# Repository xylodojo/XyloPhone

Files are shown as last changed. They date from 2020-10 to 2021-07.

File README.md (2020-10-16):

# XyloPhone
Design files and materials related to the XyloPhone platform. 

The preprint is available on bioRxiv: https://biorxiv.org/cgi/content/short/2020.08.02.233114v1

~~The manuscript is currently under review. After publication the design files for producing a XyloPhone will be disseminated here.~~

The paper has been accepted to the IAWA journal. It is an open access article and should be here (when it goes to "press"): https://brill.com/view/journals/iawa/aop/issue.xml

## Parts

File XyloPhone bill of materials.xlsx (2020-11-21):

 | XyloPhone Bill of Materials
Qty | XyloPhone part | Vendor | MFR | MFR # | Total cost | units per cost | cost per part | Cost per Scope
1 | LED controller | Digikey | Recom Power | RCD-24-0.30‎ | 13.46 | 1 | 13.46 | 13.46
1 | Voltage reference | Digikey | ‎Analog Devices Inc.‎ | AD680JTZ‎ | 5.75 | 1 | 5.75 | 5.75
1 | Radial capacitor | Digikey | Murata Electronics‎ | RDER71H104K0P1H03B‎ | 0.31 | 1 | 0.31 | 0.31
4 | White LED | Digikey | Lite-On Inc. | ‎LTPL-P00DWS57‎ | 0.76 | 1 | 0.76 | 3.04
4 | UV LED | Digikey | Vishay Semiconductor Opto Division | ‎VLMU1610-365-135CT-ND‎ | 2.38 | 1 | 2.38 | 9.52
1 | SPDT switch | Digikey | NKK Switches | MS13AFG01‎ | 4.05 | 1 | 4.05 | 4.05
2 | Right angle JST Through-Hole 2-Pin Connector | Digikey | JST Sales America | S2B-PH-K-S(LF)(SN) | 0.17 | 1 | 0.17 | 0.34
1 | JST jumper two wire assembly 6" | Digikey | Sparkfun Industries | PRT-09914 | 0.95 | 1 | 0.95 | 0.95
4 | 1/2" No. 2 screw | McMasterCarr | McMasterCarr | 95893A560 | 13.41 | 50 | 0.27 | 1.07
6 | 1/4" No. 0 screw | McMasterCarr | McMasterCarr | 95893A505 | 14.05 | 50 | 0.28 | 1.69
1 | Belomo 10x Triplet hand lens | belomostore.com | Belomo |  | 29.98 | 1 | 29.98 | 29.98
1 | battery | SparkFun | Lithium Ion Battery - 1Ah | PRT-13813 ROHS | 9.95 | 1 | 9.95 | 9.95
1 | charger | SparkFun | SparkFun LiPo Charger Plus | PRT-15217 | 9.95 | 1 | 9.95 | 9.95
1 | Reversible USB A to C Cable - 0.3m | SparkFun | SparkFun | CAB-15426 ROHS | 3.95 | 1 | 3.95 | 3.95
1 | Power distribution PCB |  |  |  | 5 | 5 | 1.00 | 1.00
1 | Power input PCB |  |  |  | 5 | 5 | 1.00 | 1.00
1 | Power output PCB |  |  |  | 5 | 5 | 1.00 | 1.00
4 | LED PCB |  |  |  | 5 | 5 | 1.00 | 4.00
 |  |  |  |  | 129.12 |  |  | 101.01

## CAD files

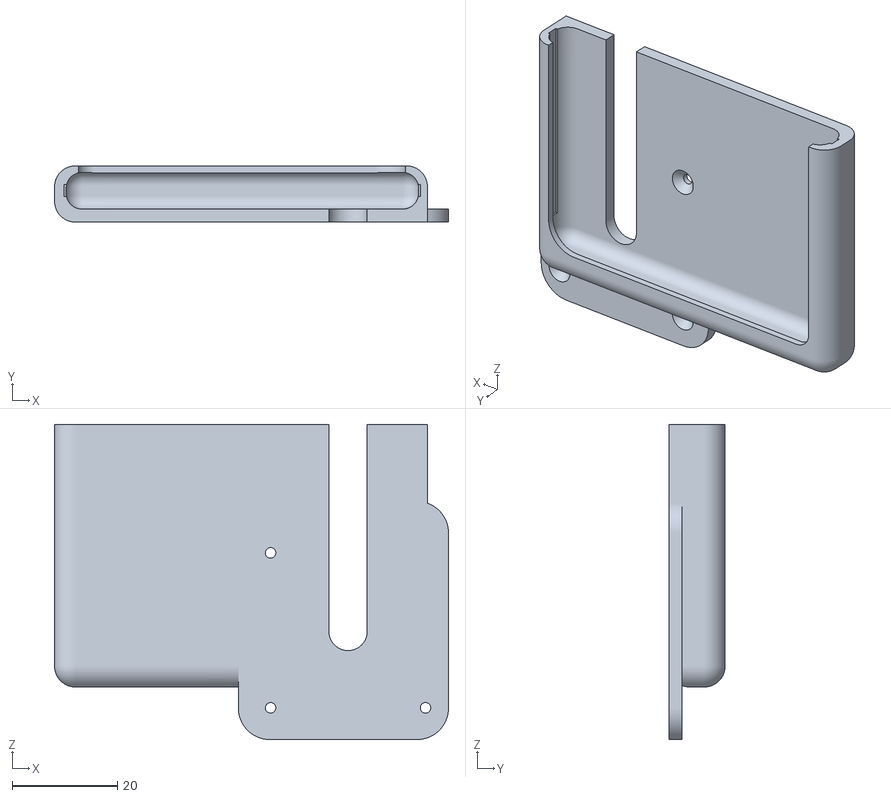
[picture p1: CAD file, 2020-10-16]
3D files/3D files/phone_adapters/iphone_6.stl
75.0 x 10.7 x 60.0

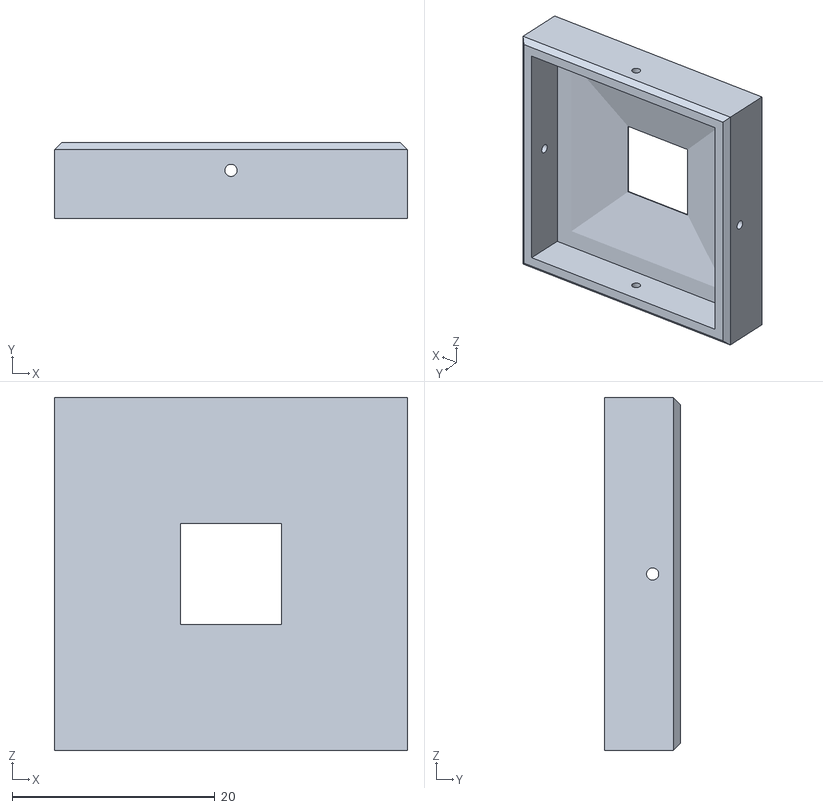
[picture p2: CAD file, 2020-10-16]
3D files/3D files/surface_plate.stl
34.8 x 7.50 x 34.8

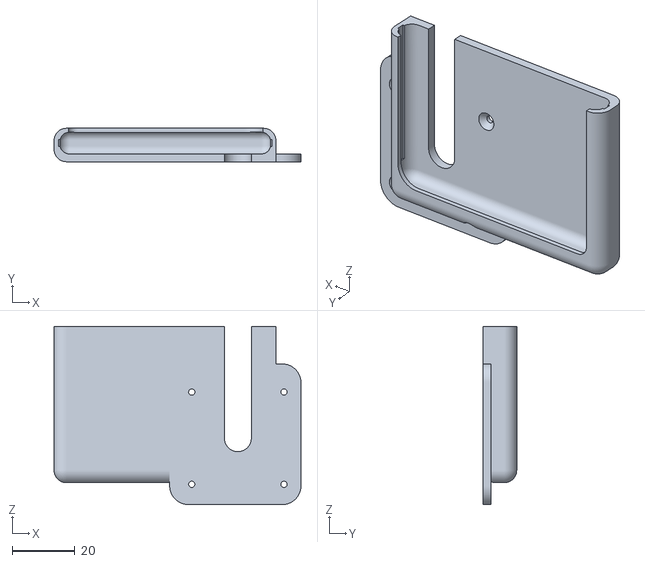
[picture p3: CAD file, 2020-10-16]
3D files/3D files/phone_adapters/iphone_8.stl
79.0 x 10.7 x 57.0

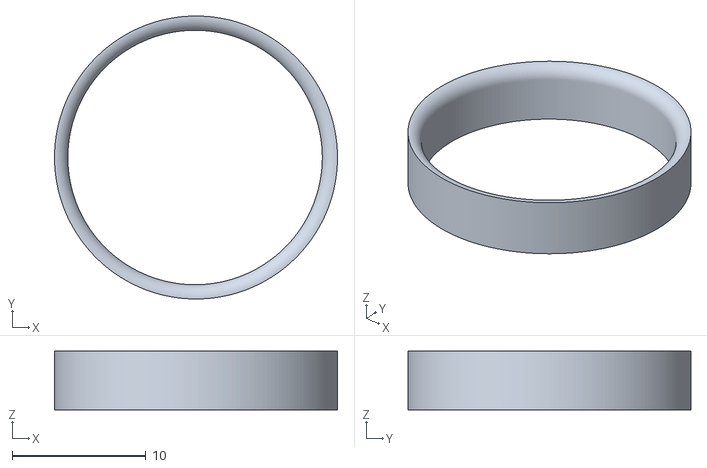
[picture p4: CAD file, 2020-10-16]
3D files/3D files/spacer_ring.stl
21.1 x 21.1 x 4.40

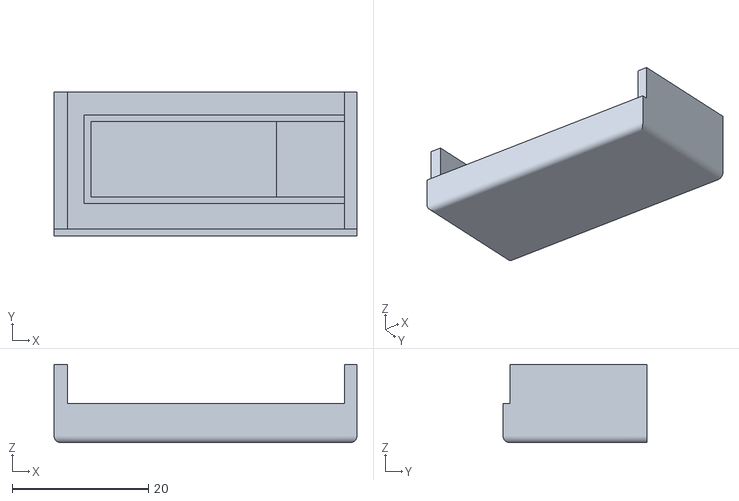
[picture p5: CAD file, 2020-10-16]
3D files/3D files/charger_cap.stl
44.4 x 21.1 x 11.5

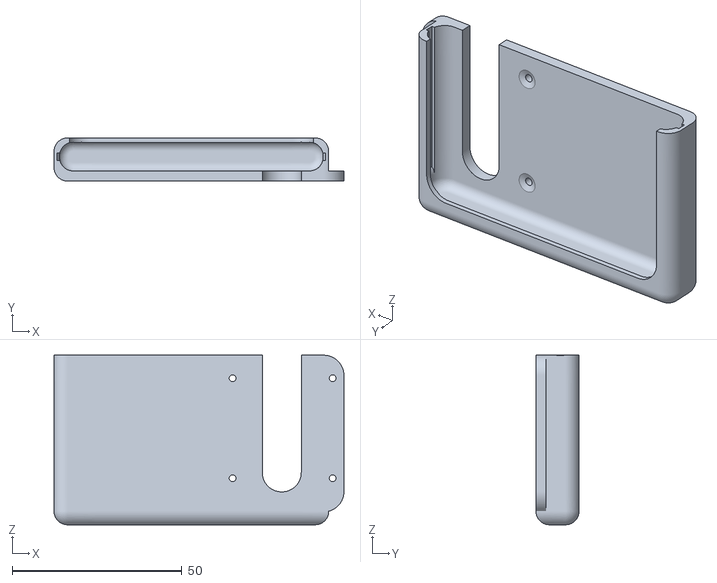
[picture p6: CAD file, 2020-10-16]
3D files/3D files/phone_adapters/iphone_XSMax.stl
85.5 x 12.7 x 50.0

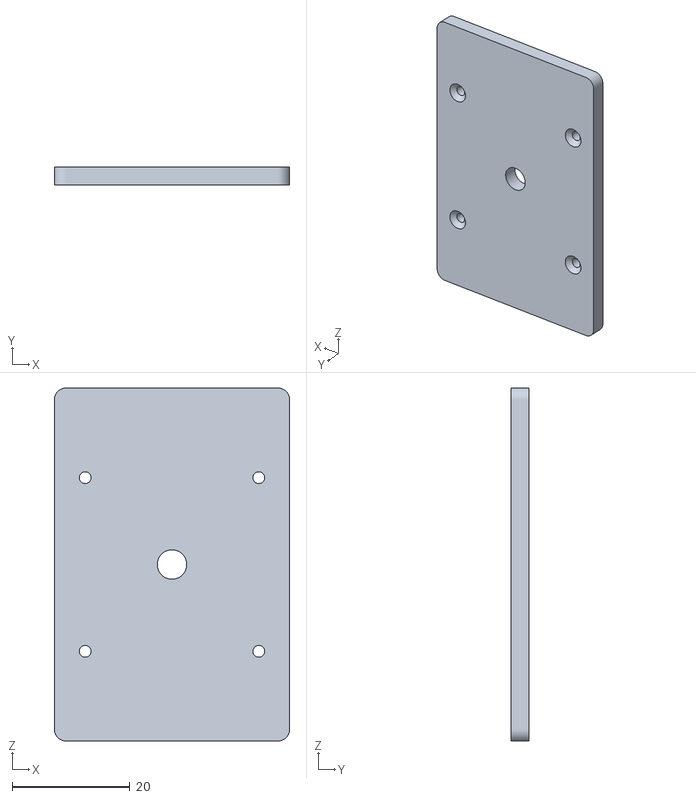
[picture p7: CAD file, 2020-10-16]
3D files/3D files/phone_adapters/generic_template.stl
40.0 x 3.00 x 60.0

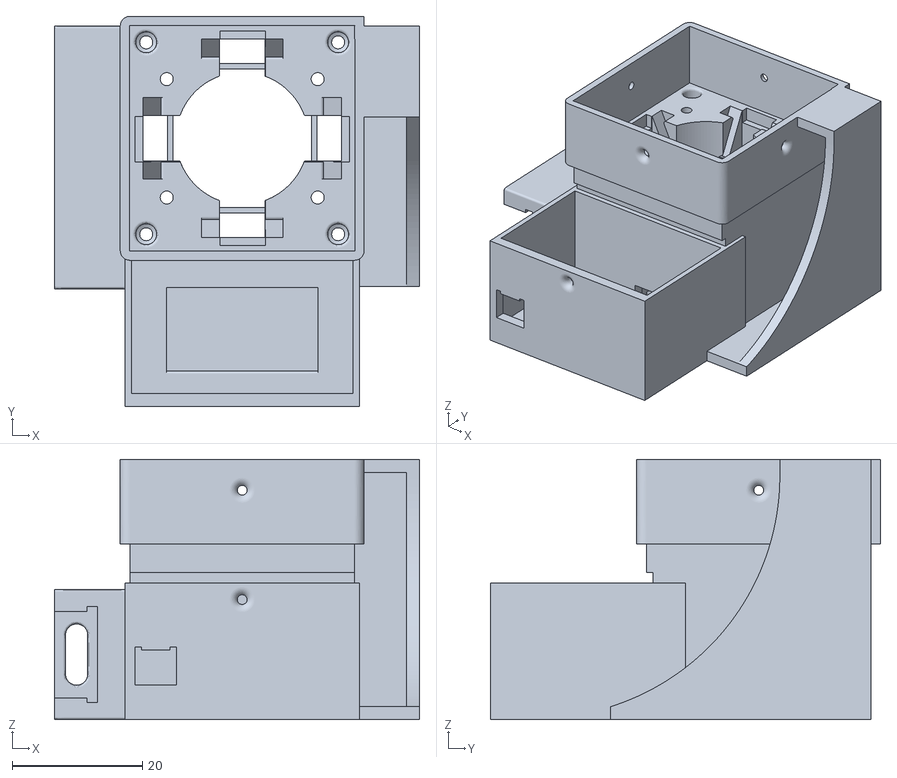
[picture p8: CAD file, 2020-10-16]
3D files/3D files/XyloPhone_housing.stl
56.1 x 60.0 x 40.0

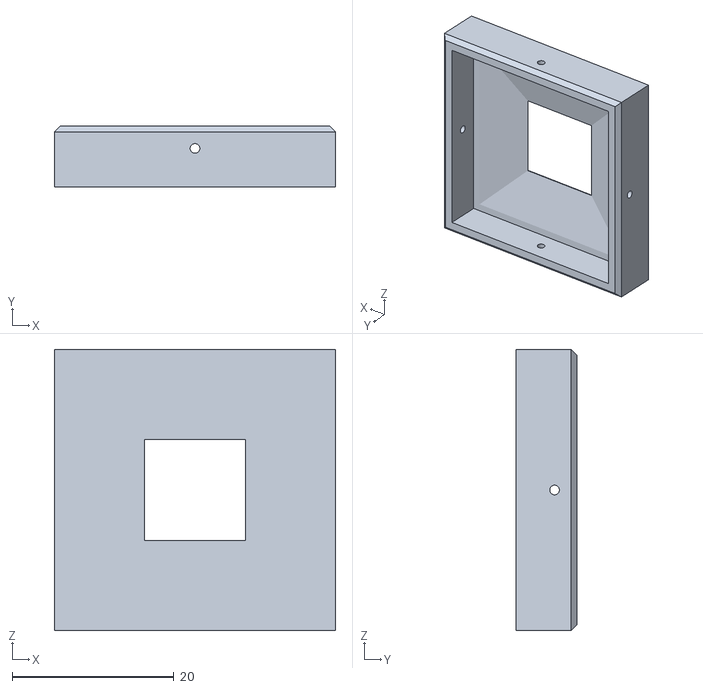
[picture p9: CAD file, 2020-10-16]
3D files/3D files/max_aperture_surface_plate.stl
34.8 x 7.50 x 34.8

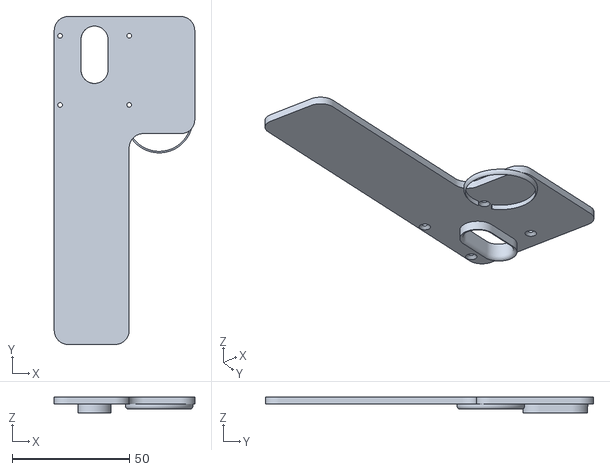
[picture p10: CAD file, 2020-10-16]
3D files/3D files/phone_adapters/iphone_XSMax_Otterbox_paddle.stl
60.0 x 140.0 x 6.70

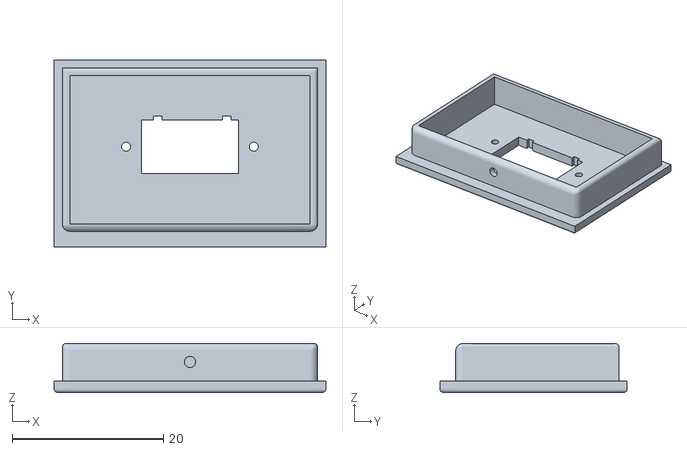
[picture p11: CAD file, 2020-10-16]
3D files/3D files/electronics_lid.stl
36.0 x 24.8 x 6.50

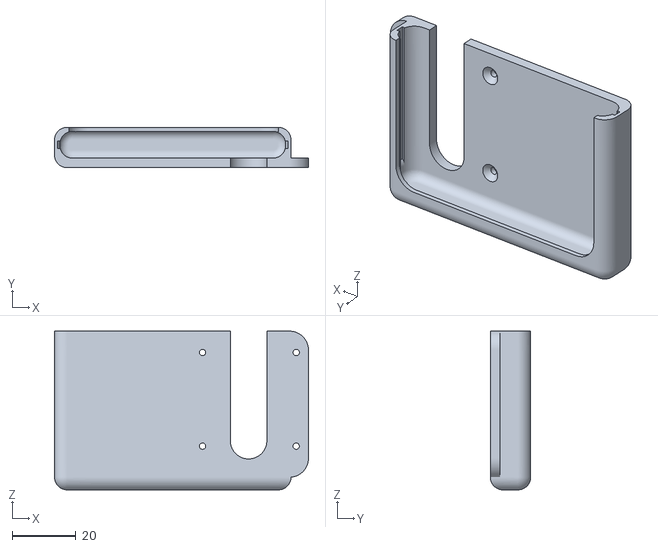
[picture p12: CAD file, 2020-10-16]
3D files/3D files/phone_adapters/iphone_XS.stl
80.0 x 12.7 x 50.0

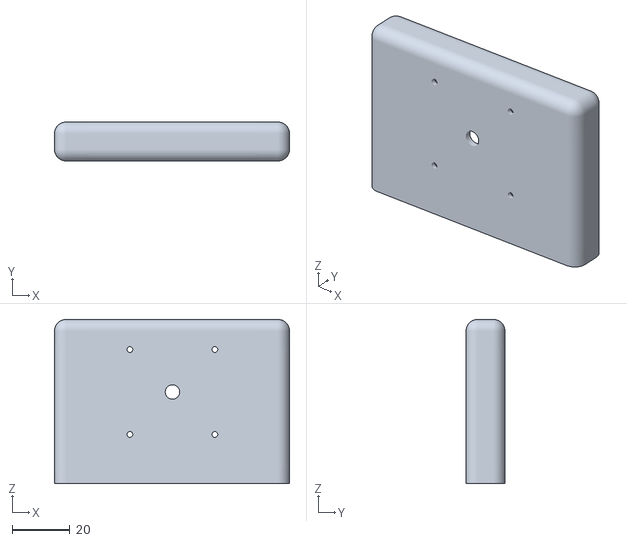
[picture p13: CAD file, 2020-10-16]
3D files/3D files/phone_adapters/samsung_Note5.stl
81.6 x 13.5 x 57.0

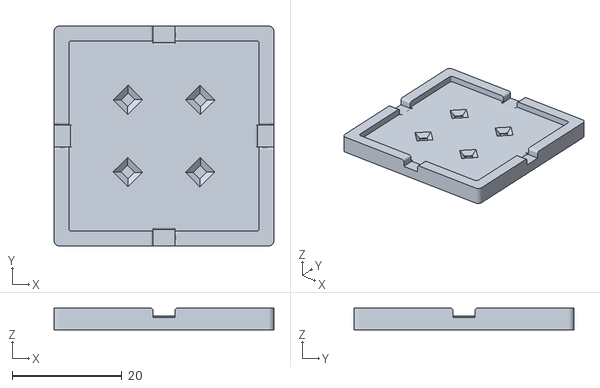
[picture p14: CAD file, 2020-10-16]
3D files/3D files/UV mounting jig.stl
40.0 x 40.0 x 4.00

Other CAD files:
3D files/3D files/phone_adapters/iphone_7Plus.stl

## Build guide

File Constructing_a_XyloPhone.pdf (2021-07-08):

# Constructing a XyloPhone

Alex C. Wiedenhoeft
Caitlin Gilly

Center for Wood Anatomy Research, Forest Products Laboratory US Forest Service, US Department of Agriculture

October 2020

Those portions of this manual recycled from the XyloTron assembly manual by Wiedenhoeft and Kleinschmidt (2020) are used here with permission of the authors.

TABLE OF CONTENTS

Part One: The Need for and Use of This Manual

Part Two: Bill of Materials

Part Three: Illustrated Parts List and Preparatory Work

Part Four: Step-by-Step XyloPhone Assembly and Calibration Instructions

PART ONE: THENEED FOR AND USE OF THIS MANUAL

The XyloPhone you are about to build is the next generation of imaging hardware for the broader XyloTron platform, leveraging the electronics of the XyloScope, but in a compact new design to accommodate bring-your-own-device functionality. The XyloPhone’s design reflects the intent that this device can be built by an enterprising end-user to image a wide range of substrates – it is an assemblage of individually simple off-the-shelf (itemized in the bill of materials in Part Two) and 3D printable components. With a phone-specific adapter it can be used on virtually any smartphone.

In Part Three we present an illustrated parts list and a short description of preparatory work that should be done prior to assembly. In this section we also note with an * several parts for which it is prudent to acquire more than the minimum number, because, if a mistake is made and the part is ruined, having spares facilitates the efficient completion of your XyloPhone. Fortunately, those components most likely to be ruined in the learning process are among the most affordable.

The step-by-step instructions in Part Four are relatively detailed. Despite this, the manual does assume certain basic skills. Specifically, no instruction on the use of basic tools (screwdrivers, cutting tools) is provided, nor is there any tutorial in stripping wires or soldering electronic components. Such tutorials abound (e.g. learn.sparkfun.com). We further assume basic functionality in 3D printing and that, if a printed component is faulty or damaged, such components can be readily reprinted.

This manual is intended to provide detailed instructions to assemble the XyloPhone in its current incarnation. It also lays the groundwork for a novice to make special modifications themselves to adapt the XyloPhone for the widest possible breadth of uses. We look forward to a future where other workers develop and share designs superior to what we provide here, and we hope to benefit from those advancements.

Each part or component is given a number in the illustrated part list. In the assembly instructions, the list number of each part is presented in parentheses beside the part’s name in the text so that should one experience any confusion, it can easily be remedied by consulting the list.

PART TWO: BILL OF MATERIALS

The bill of materials to build one XyloPhone. Minimum required quantity (Qty), XyloPhone part name, Vendor, Manufacturer (MFR), and manufacturer part number (MFR #) are listed. Please refer to the notes in Part Three for those parts for which acquiring more than the minimum possible number might be advisable. One will also need a smartphone, and to adapt a holder for that phone.

Qty | XyloPhone part | Vendor | MFR | MFR #
1 | LED controller | Digikey | Recom Power | RCD-24-0.30
1 | Voltage reference | Digikey | Analog Devices Inc. | AD680JTZ
1 | Radial capacitor | Digikey | Murata Electronics | RDER71H104K0P1H03B
4 | White LED | Digikey | Lite-On Inc. | LTPL-P00DWS57
4 | UV LED | Digikey | SunLED | XZVS54S-9A
1 | SPDT switch | Digikey | NKK Switches | MS13AFG01
2 | Right angle JST Through-Hole 2-Pin Connector | Digikey | JST Sales America | S2B-PH-K-S(LF)(SN)
1 | JST jumper two wire assembly 6" | Digikey | Sparkfun Industries | PRT-09914
4 | 1/2" No. 2 screw | McMasterCarr | McMasterCarr | 95893A560
7 | 1/4" No. 0 screw | McMasterCarr | McMasterCarr | 95893A505
1 | 1/4" No. 2 screw | McMasterCarr | McMasterCarr | 95893A550
1 | Belomo 10x Triplet hand lens | belomostore.com | Belomo
1 | Lithium ion battery | SparkFun | Lithium Ion Battery - 1Ah | PRT-13813 ROHS
1 | Battery charger | SparkFun | SparkFun LiPo Charger Plus | PRT-15217
1 | Reversible USB A to C Cable -0.3m | SparkFun | SparkFun | CAB-15426 ROHS
1 | Power distribution PCB
1 | Power input PCB
1 | Power output PCB
4 | LED PCB

PART THREE:NUMBERED AND ILLUSTRATED PARTS LIST ANDPREPARATORY WORK

NUMBERED AND ILLUSTRATED PARTS LIST (NUMBER REQUIRED WITHIN PARENTHESES, * DENOTES PRUDENCE IN ACQUIRING MORE THAN THE MINIMUM NUMBER). IMAGES ARE NOT TO SCALE.

1. 3D printed XyloPhone housing
2. 3D printed charger cap
3. 3D printed electronics lid
4. 3D printed spacer ring
5. 3D printed surface cap

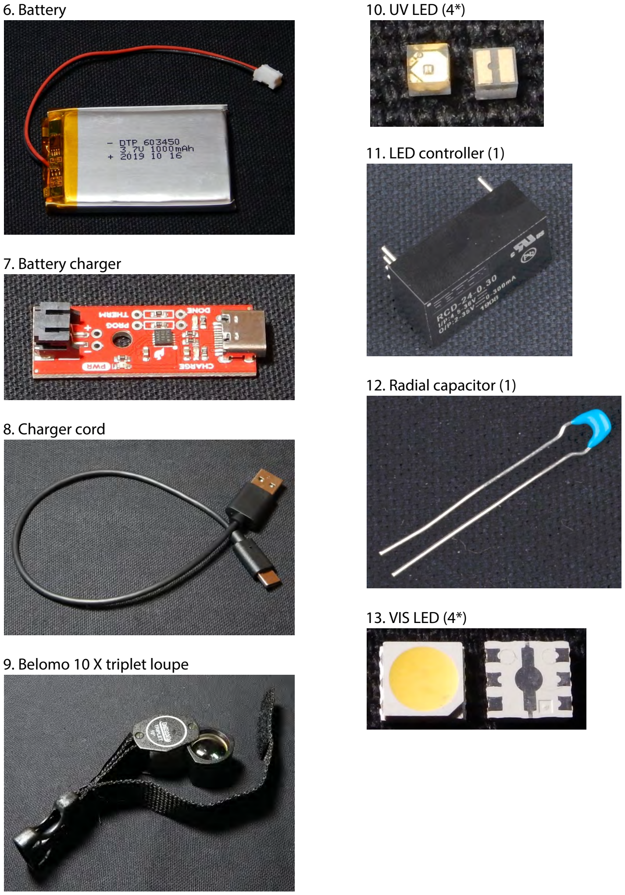
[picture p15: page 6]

6. Battery
7. Battery charger
8. Charger cord
9. Belomo 10 X triplet loupe
10. UV LED (4*)
11. LED controller (1)
12. Radial capacitor (1)
13. VIS LED (4*)

14. Switch (1)
15. Right angle JST Through-Hole Connector (1*)
16. (a, b, c)
(a) 1/2” No. 2 screw
(b) 1/4” No. 2 screw
(c) 1/4” No. 0 screw
17. Voltage reference (1)
18. JST jumper two wire assembly 6" (1)
19. Power distribution PCB – top view only (1*)
20. Power input PCB – top view, bottom view (1*)
21. Power output PCB– top view, bottom view (1*)

22. LED PCB (4*)
Note that for all PCBs, + through holes are round or have rounded corners, and – through holes are squares or have right-angle corners.

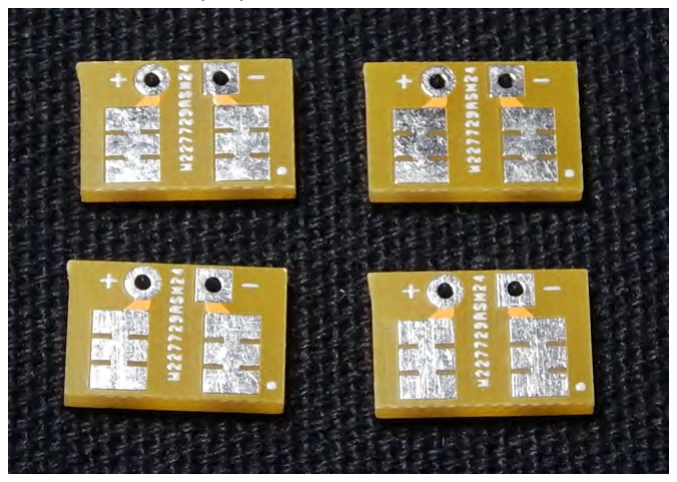
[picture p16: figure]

23. Jig for soldering UV LEDs

PREPARATORY WORK
Print the 3D printed components. Clean them of any adhesive used in the printing process, and also do any trimming necessary - it is common that the plate face of the 3D printed component will have a lip that is slightly wider than the rest of the part (shown below via the end view of a freshly printed object printed in black polymer). This can be removed with a utility knife or a deburring tool.

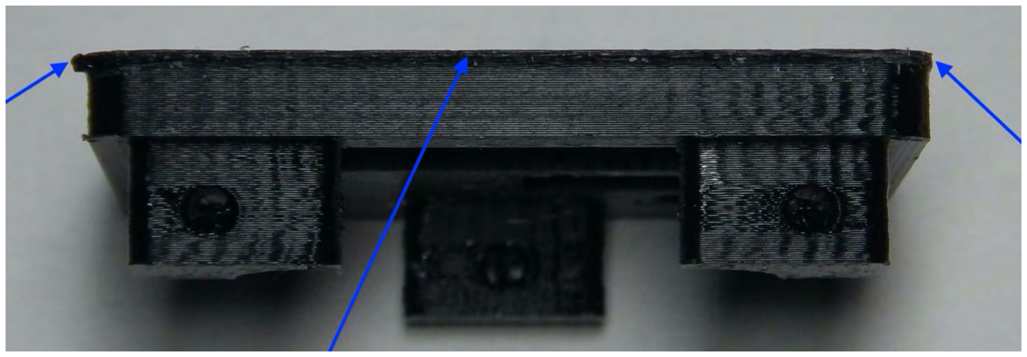
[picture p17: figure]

In the illustrations of this manual, there are only five 3D printed components, all of which were printed in white polymer to facilitate photographing the assembly process. It is recommended that in practice all components be printed in black to prevent any white-balance distortion.

Submit the Gerber files to order the printed circuit boards. We have printed the boards in red and white and in tan, but other color combinations are possible. Perhaps the most conservative selection would be black boards with dark grey printing so that the boards themselves cannot cause white-balance distortion.

Remove the lens from the Belomo 10 X triplet loupe (9). Open the loupe and find the side that has the internal nut holding the lens in place. Using a tool like an internal snap ring pliers, unscrew the nut and remove the lens.

PART FOUR: STEP-BY-STEP XYLOPHONEASSEMBLY INSTRUCTIONS

ELECTRONIC COMPONENTS – SOLDERING AND WIRING, PHASE I

Power input assembly

1. Clamp the LED controller (11) in a vise, pins-side up
2. Fit the power output PCB (21) onto the two pins on the LED controller (11). The power output PCB (21) has a partial rectangle printed to show where the controller seats – that printed side will be in contact with the LED controller (11), so there is only one way this board can be placed (note that the below left we are showing the face that will be in contact with the LED controller (11)). Below right we show the correct installation onto the two pins of the LED controller (11). Solder the two pins, then flush cut them.

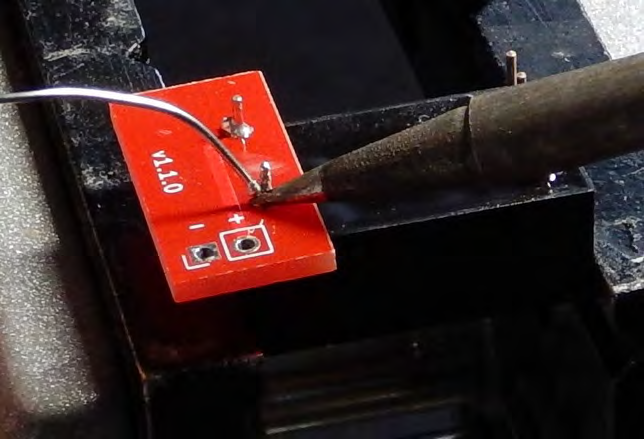
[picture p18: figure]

3. Fit the power input PCB (20) onto the four pins on the LED controller (11). As with the power output PCB (21), the power input PCB (20) has a partial rectangle printed to show where the LED controller (11) seats (note in the image below-left: we are showing the face that will be in contact with the LED controller (11)). Below-right: we show the correct installation onto the four pins of the LED controller (11) – note that the partial circle print is now facing up (lower right image). Solder all four pins, then flush cut them.

4. Insert the voltage reference (17) into the three holes in the power input PCB (20). There is a semicircular print with a flat edge associated with the three mounting holes on the board. Install the voltage reference (17) so that its flat face is facing the flat side of the shape outline. Gently and carefully bend the leads so that the bottom of the voltage reference (17) can be mounted within 2-3mm of the top surface of the power input PCB (20). Solder the three leads separately and flush cut them. If the voltage reference (17) is mounted too high, the assembly will not fit in in later steps.
5. Insert the radial capacitor (12) into the two holes in the small printed rectangle (labeled C1) so that its height is less than that of the voltage reference (17). There is no special orientation for the radial capacitor (12). Solder and flush cut.
6. The last component of the power input PCB (20) is the right angle JST through-hole connector (15). This fitting is inserted from the LED controller (11) side of the power input PCB (20) so that its pins emerge by the printed – and + near the radial capacitor (12). Solder these two pins, taking care to make mechanically strong connections with the board without angling the pins or melting through to the plastic housing. Flush cut the pins.

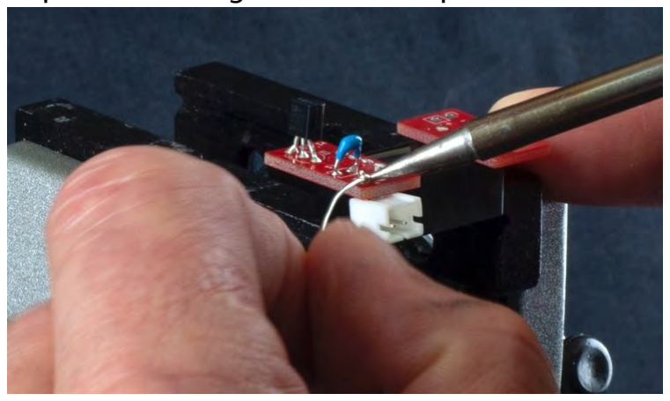
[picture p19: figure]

VIS LED-LED PCB assemblies

7. Pinch the VIS LED (13) onto the LED PCB (22) with flat tweezers, and then use a small binder clip to holder the tweezers in place. The compliance of the tweezers ensures that excessive force is not applied to the VIS LED but permits fine spatial adjustment of the VIS LED (13) position on the LED PCB (22). (The VIS LED (13) is best placed about 0.5mm from the outer edge of the LED PCB (22) and the small cut-out on the corner of the VIS LED (13) must face the outer edge of the – pad (left image, below)). This assembly is then clamped in the vise. Heating the soldering pads of the LED PCB (22) without touching the VIS LED (13) and then allowing capillary flow to make the connection is usually successful. It is important to use a minimal amount of solder so that the VIS LED-LED PCB assemblies will slide smoothly into the 3D printed XyloPhone housing (1). Repeat this process three more times, for a total of four completed VIS LED-LED PCB assemblies.

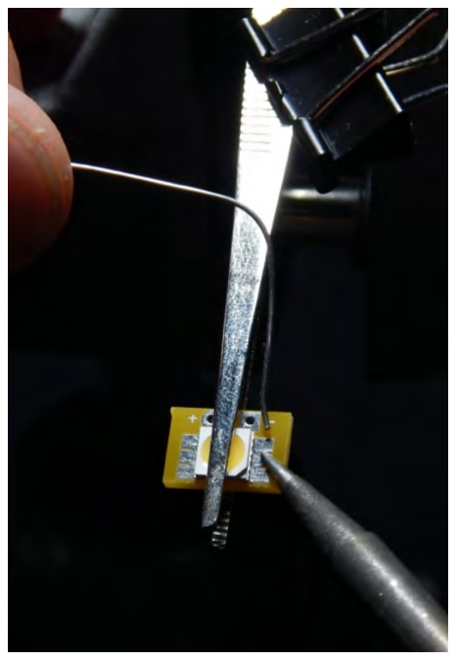
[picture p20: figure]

8. Using an LED testing setting on a multimeter, ensure that each VIS LED-LED PCB assembly lights both internal LEDs in the VIS LED (13). This is best done at the +/- through holes on the LED PCB (22), to ensure the entire assembly is electrically correct.

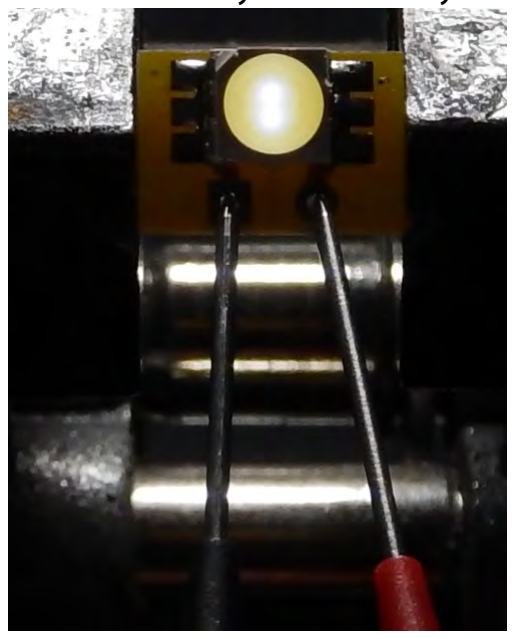
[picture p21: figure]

9. Insert the twisted stranded wire into each through hole on the VIS LED PCB (22). Solder the wires in the through holes. Flush cut the back side of the boards, then trim the excess wire to no less than 7mm.
10. Twist the wire as you strip the insulation from the ca. 7mm of wire, ensuring that it is tightly twisted. Lightly tin this now-bare wire ensuring that that you do not increase the outer diameter of the braid- it must be able to pass through the through-holes in the power distribution PCB (19).

11. Given the difficulty of mounting the electronics into the 3D printed XyloPhone housing (1) in a later steps, it would be prudent to use a multimeter to test each VIS LED (as in step 8), using the electrodes on the tinned wires. These connections will become inaccessible in later steps.

Power distribution PCB-UV LED assembly

12. Place the UV LED soldering jig (23) on a firm, level, heat-tolerant surface.

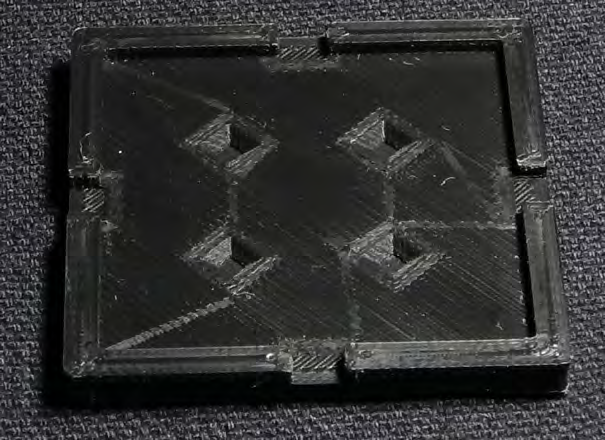
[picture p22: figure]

13. There are four depressions in the jig – you will place one UV LED (10) in each of the depressions, oriented so that the soldering pads are facing up (the light emitting face is down into the depressions) and the positive pad is clockwise as you look down, or to the right, relative to the center of the UV LED soldering jig (23). The UV LEDs are small and fragile – please use forceps and great care in placing them.
14. Place the power distribution PCB (19) into the UV LED soldering jig, so that the UV, VIS, GND, and NC prints are face-down. Using even pressure across all four edges, snap the power distribution PCB (19) into the UV LED soldering jig (23), securing the four properly oriented UV LEDs (10) in the depressions.

15. Secure the power distribution PCB (19) to the UV LED soldering jig (23) with four small binder clips, one on each edge.
16. Using seemingly-excessive force (e.g ~4kg or ~9 lbs.), push the soldering iron firmly down at a slight angle into one of the through-holes (D5-D8) in the power distribution PCB (19), leaving a small space for capillary flow of solder. Pushing the soldering iron firmly downward, flood the through-hole with a significant excess of solder, then continue to push the soldering iron downward until the solder flux boils. Move to the adjacent through-hole and repeat - this second through hole usually solders much more quickly because the board is already locally heated. Repeat for the remaining three peninsulas.

17. Using small movements and great care, pry each side of the power distribution PCB (19) directly upward a tiny (less than 1mm) amount with a small flat-head screwdriver, rotating the UV LED soldering jig (23) 90 degrees each time until the power distribution PCB (19) lifts out of the UV LED soldering jig (23). If all went as planned, all four UV LEDs (10) will be firmly soldered to the power distribution PCB (19). If not, carefully place the power distribution PCB
(19) back into the UV LED soldering jig (23), and repeat steps 15-16 for the loose UV LED (10), using even greater downward force and additional solder.
18. Before proceeding, it is a good idea to confirm that your soldering work is sound and electrical connections are made correctly. This is most easily done by using the power input assembly completed in Step 6 to power the power distribution PCB-UV LED assembly. Plug the JST male connector of the Battery (6) into the female JST connector (15) on the power input board (20). There is but one way to accomplish this, so it is not pictured.
19. Using the JST jumper two wire assembly (18), push the pins through the through holes on the power output PCB (21) ensuring that the red wire is connected to the + through hole and the black wire is connected to the - through hole.

20. Please wear UV-protective eye protection prior to completing this step! Ensuring that the pins of the JST jumper two wire assembly (18) are in contact with the through holes of the power output PCB (21), touch the black (-) wire to the GND corner’s large through hole, and the red (+) wire to the UV corner’s large through hole on the power distribution PCB-UV LED assembly. If all electrical connections are correct, all four UV LEDs (10) will light up. Remove the JST jumper two wire assembly (18) if all is well. If one or more UV LEDs (10) fail to light, proceed to step 21, otherwise proceed to step 22.
21. Sometimes one pad of the UV LED (10) does not have a good electrical connection (only one UV LED (10) shown in the image). To solve this, place the solder at an angle to the pad of the UV LED (10) that is not connected, and WITHOUT TOUCHING THE LED WITH THE SOLDERING IRON, solder the pad of the UV LED (10). Repeat these steps for any other UV LEDs (10) lacking connection.

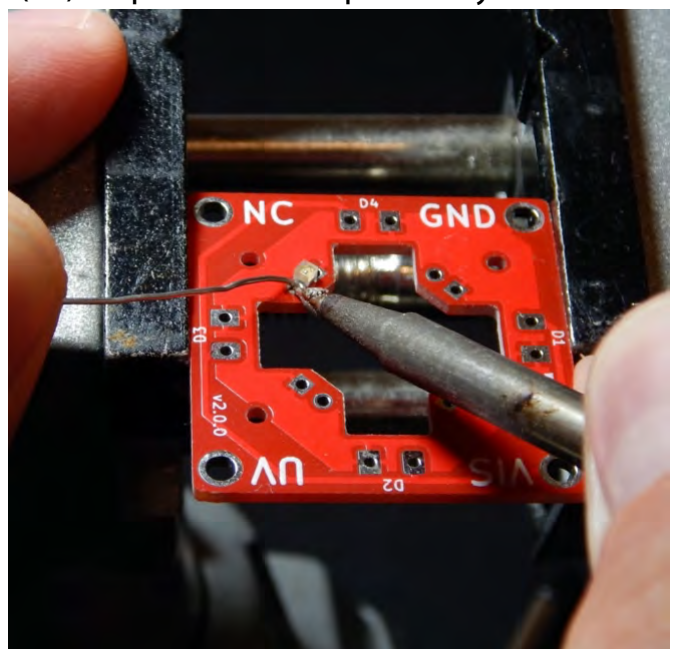
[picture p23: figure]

22. When all UV LEDs emit when powered, the power distribution PCB-UV LED assembly is complete for now.

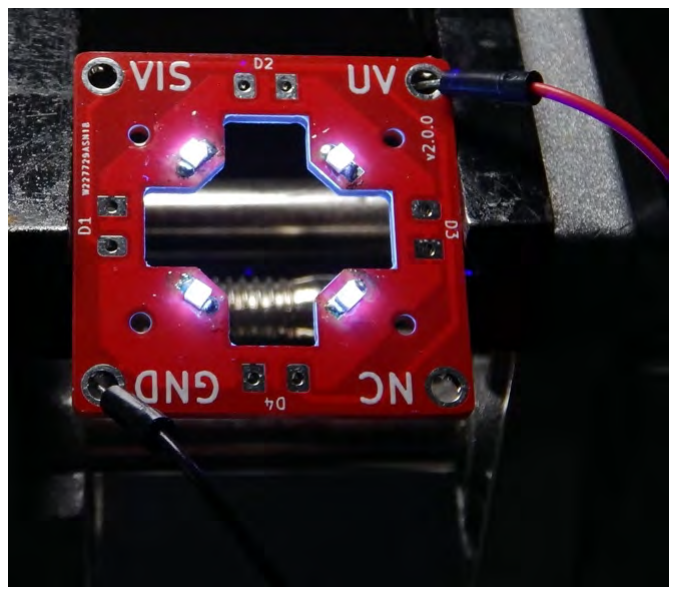
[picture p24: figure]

MECHANICAL ASSEMBLY – PHASE I

LED holder-power distribution PCB assembly

23. Now that the UV LEDs (10) are soldered onto the power distribution PCB-UV LED assembly it is important that as you handle the assembly you do not damage the UV LEDs (10). They are well-suited to thousands of hours of data collection, but are not resilient in the face of mechanical damage. Insert each of the four VIS LED-LED PCB assemblies into the bottom face of the power distribution PCB (19) such that the VIS LED (13) is facing the center cut-out in the power distribution PCB (19). This will ensure that the – and + terminals on each of the boards match.

Read this entire step prior to starting, as board orientation with regard to the 3D printed XyloPhone housing (1) is critical

24. Using great care not to damage the UV LEDs (10), tip the 3D printed XyloPhone housing (1) sideways, and push the VIS LED – LED PCB -power distribution PCB-UV LEDs assembly into the large rectangular manifold at the top of the 3D printed XyloPhone housing (1). The VIS LED-LED PCBs will enter the manifold first, and each will slide into an angled slot to orient them correctly. Each board will need to be manipulated separately into its slot, and this process is made easier by the horizontal orientation of the 3D printed XyloPhone housing (1) and can be facilitated by the judicious use of fine-tipped forceps. The ~7mm of wire soldered to each VIS LED-LED PCB should provide ample play to situate each assembly without it slipping from the power distribution PCB. The rotation of the power distribution PCB with regard to the 3D printed XyloPhone housing (1) is critical. We have found it easiest to orient the board as depicted below, but please note this orientation (vs. 180 degrees, which the only other functional option) necessitates a longer UV and VIS power supply wire path in later steps. In my mind, we have preferred this longer path length and a power distribution PCB orientation that favors the printed text of UV and VIS on the corners of the power distribution PCB in an “upright” position, but that is an entirely biased view based on my preferred (and arbitrary) “up” orientation for the 3D printed XyloPhone housing (1). (A wiring parsimonist would clearly prefer a frame of reference inverted relative to my preference, and given those assumptions, they are completely correct.) Once the VIS LED -LED PCBs are fully seated in their slots, carefully but forcefully press the power distribution PCB into the manifold until it is flush across its entire face. It is all too easy to damage the UV LEDsin this phase. Ensure that the holes in the power distribution PCB nearest the UV LEDs are aligned with the holes in the 3D printed XyloPhone housing (1). These are necessary for routing power in subsequent steps. If these holes are not aligned, the power distribution PCB and VIS LED-LED PCB assemblies will need to be carefully extracted, rotated 90 degrees, and re-installed.

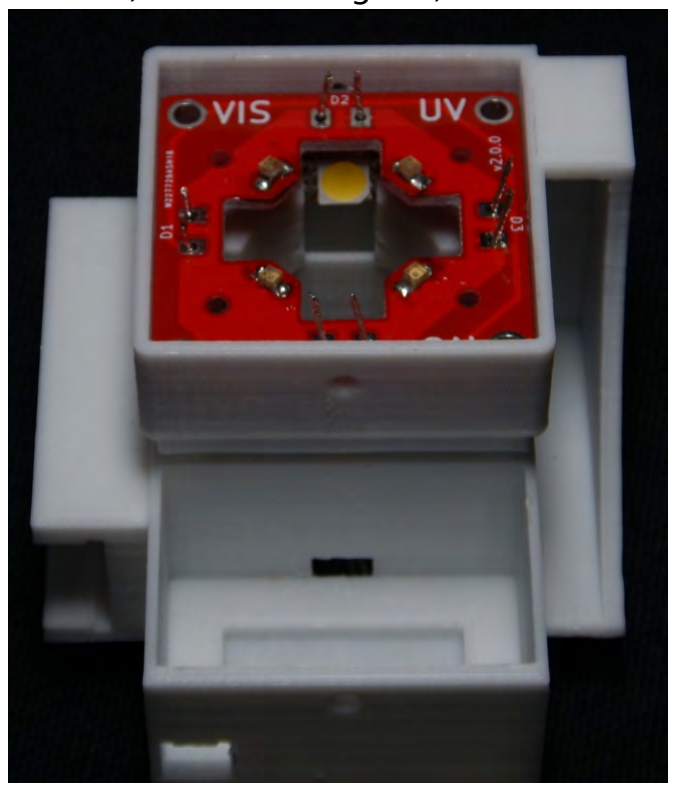
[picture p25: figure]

ELECTRONIC COMPONENTS – SOLDERING AND WIRING, PHASE II

LED holder-power distribution PCB assembly

25. The ~7mm wires soldered to each VIS LED board are now protruding from the top face of the power distribution PCB. Taking great care not to touch the soldering iron to the 3D printed manifold, solder each wire in the through hole and flush cut.
26. As with Steps 16-18, it is prudent (and satisfying) to confirm that the electrical connections are sound. Using the same assembly in Steps 16-18, and ensuring that the pins of the JST jumper two wire assembly (18) are in contact with the through holes of the power output PCB (21), touch the black (-) wire to the GND corner’s large through hole, and the red (+) wire to the VIS corner’s large through hole on the power distribution PCB-UV LED assembly. If all electrical connections are correct, all four VIS LEDs (13) will light up. Remove the JST jumper two wire assembly (18) if all is well. If one or more VIS LEDs (13) do not light, check the connections at the through-holes to the power distribution PCB (19).

WIRING THE POWER DISTRIBUTION PCB

27. Through the small holes near each UV LED (10), feed a narrow (e.g. 28 ga. stranded insulated) wire through the holes adjacent to the GND, UV, and VIS large corner through-holes. The wires must be long enough (e.g. ~16 cm) to reach the corner through holes on the top of the 3D printed XyloPhone housing (1), and must be long enough to route through the channels in the base, and into the electronics compartment on the front of the 3D printed XyloPhone housing (1).

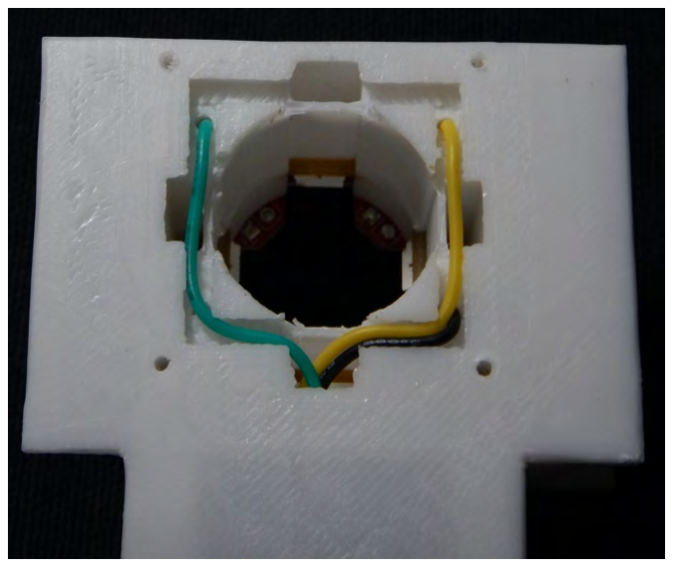
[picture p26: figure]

28. Strip insulation from the end of each wire, twist the end, and form a small coil or ball that can be tucked into the large corner through hole in the power distribution PCB (19). Taking great care not to melt the manifold, solder each wire to the corner through holes.

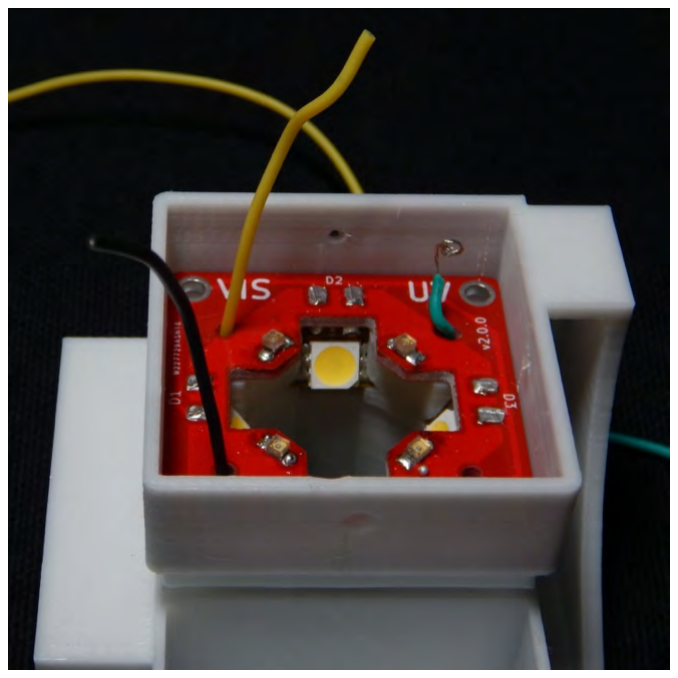
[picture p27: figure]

29. Flip over the 3D printed XyloPhone housing (1) and route the wires through the channels in the base, and out the small opening into the electronics compartment. Securing the wires with an even layer of clear tape that does not obscure the central cylindrical opening is convenient. When the wires are routed correctly they will look something like what is shown below (arrow indicating the clear tape).

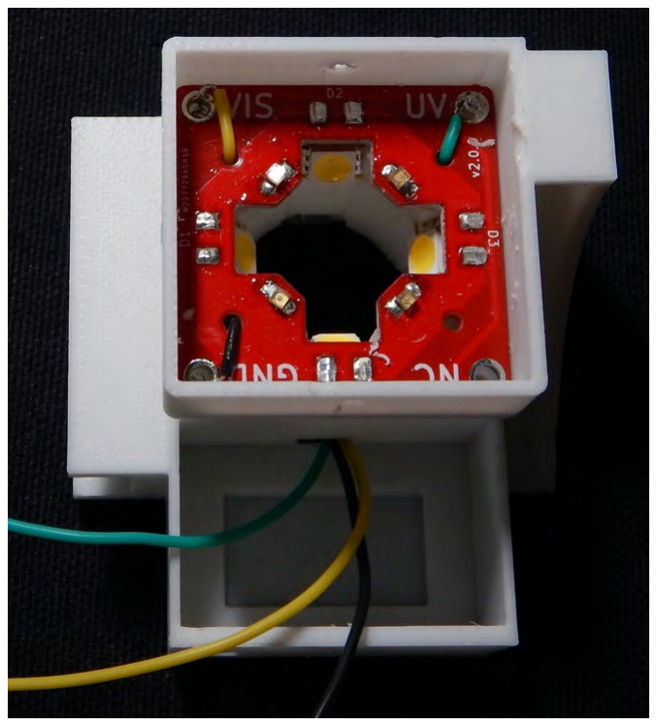
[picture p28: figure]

30. Install the power input assembly in the electronics compartment. Pull aside the wires and angle the assembly so that the JST connector (15) can protrude through the printed hole in the outer wall of the electronics compartment. The LED controller (11) will snap into the printed recess in the base of the compartment. It will be a snug fit, and lightly sanding off or trimming the right angle of the rear edge of the LED controller (11) can facilitate this.

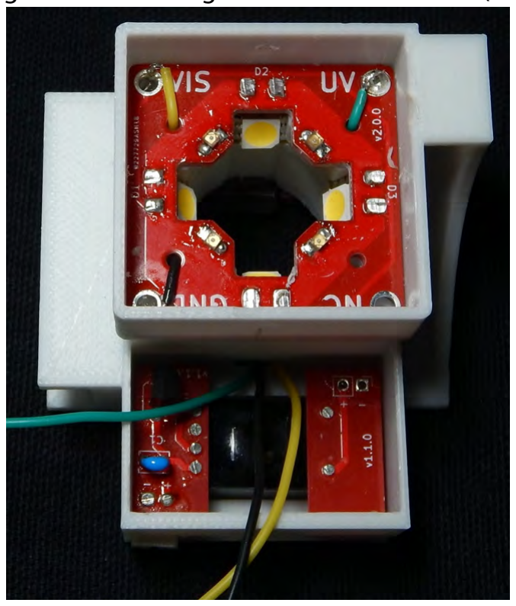
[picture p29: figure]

31. Wire the GND wire (black in the images here) to the – through hole on the power output PCB (21). Trim the black to wire to a suitable length, strip, twist and solder.

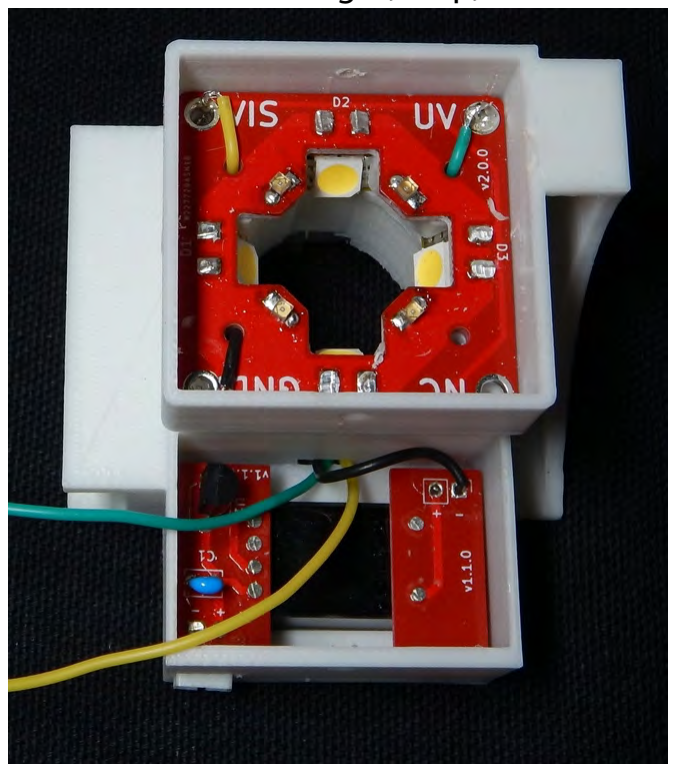
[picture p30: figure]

32. Cut a suitable length of wire (e.g. ~4cm) to be soldered to the + through hole on the power output PCB (21) – we used a red wire. This wire will connect to the center terminal on the switch (14). Strip, twist and solder to the + through hole.

33. Fit the switch (14) into the printed slot in the 3D printed electronics lid (3), then slide one piece of shrink tubing up each of the three wires – do not let them come too close to the switch (15) or the heat of soldering will cause premature shrinkage. Trim the wires as short as will permit you to wire them to the switch (14) and still manipulate the 3D printed electronics lid (3). Strip the end of the wire connected to the + terminal of the power output PCB (21)(red in the images here), twist, pull it through the center terminal on the switch (14), mechanically twist it to the terminal, then solder in place. Repeat this wire stripping and soldering for the remaining two wires (one yellow “VIS” and one green “UV”) to the remaining two lateral terminals. Allow the wires and posts to cool. Slide the shrink tubing down over the cooled, soldered terminals. Carefully shrink the tubing with a heat gun – the heat gun can easily melt 3D printed electronics lid (3) or the 3D printed XyloPhone housing (1) so some care is needed.
34. Snap the 3D printed electronics lid (3) into place, taking care that the shallower lip is seated in the slot in the 3D printed XyloPhone housing (1). It requires some force to make this fit. Secure the 3D printed electronics lid (3) with a ¼” No. 0 screw (16c), and use two more to secure the switch.

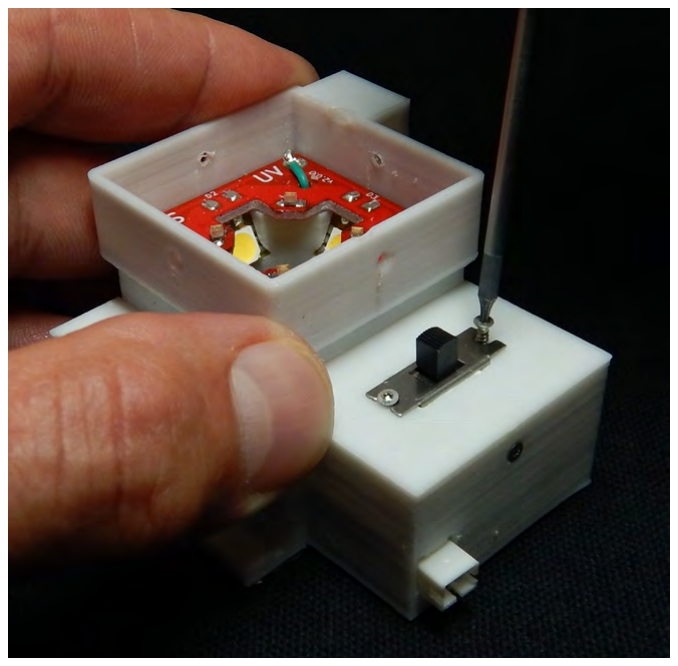
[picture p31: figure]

35. Install the 3D printed surface cap (5) into the manifold in 3D printed XyloPhone housing (1). If the power distribution PCB (19) was installed perfectly flush with the internal supports, the 3D printed surface cap (5) should snap in similarly flush. The fit is quite snug, and in reality there is probably little need for it, but using four ¼” No. 0 screws (16c), secure the 3D printed surface cap (5).

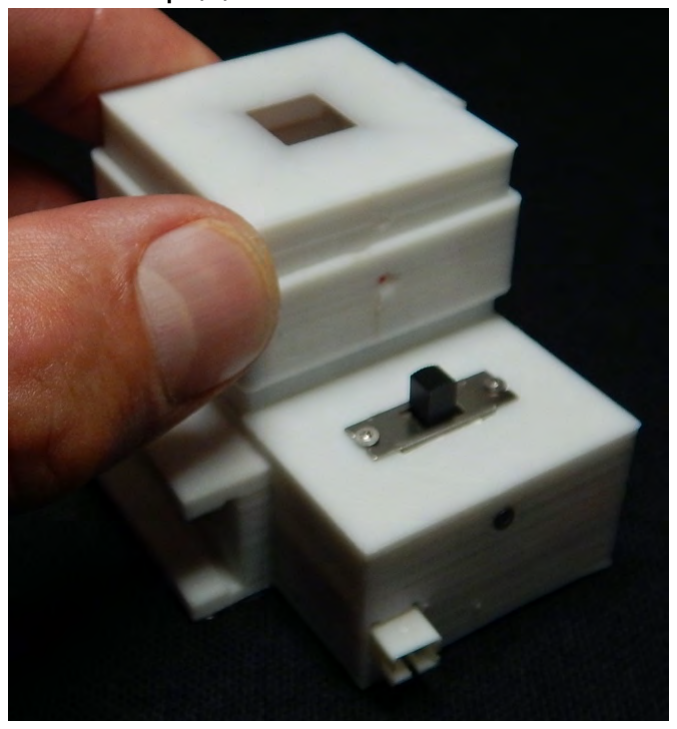
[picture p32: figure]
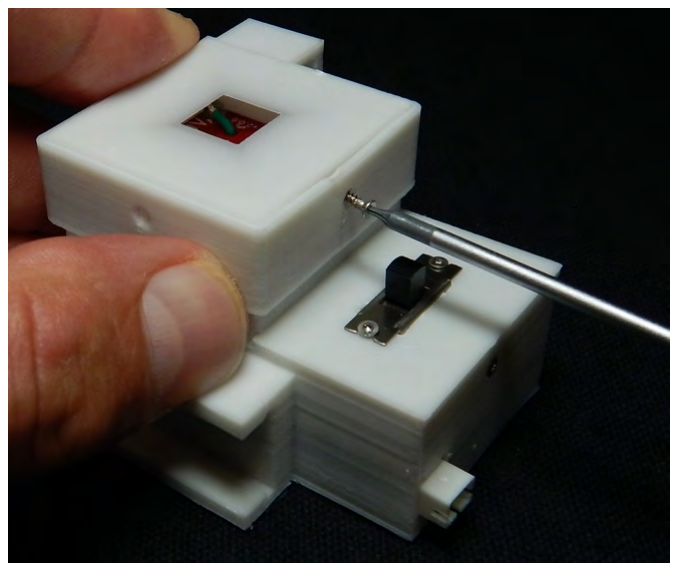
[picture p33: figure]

36. Slide the battery charger (7) into the charger slot in the 3D printed XyloPhone housing (1). The oval USB-C end of the battery charger (7) slides in first to mate with the oval printed hole. When the charger is fully seated, secure it with a ¼” No, 2 screw (16b).

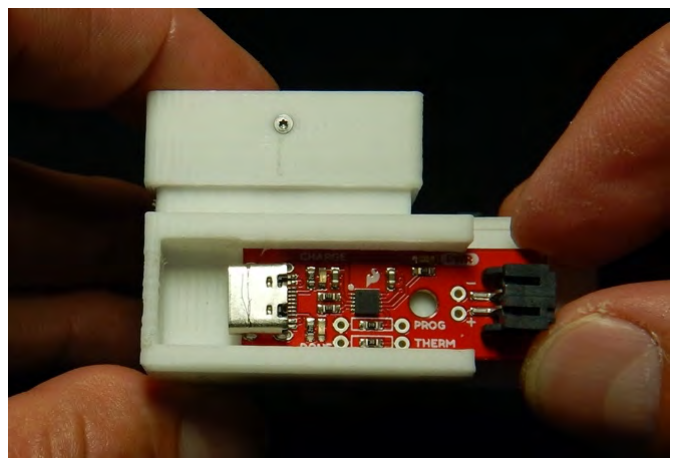
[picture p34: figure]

37. Snap the charger cover over the charger. Note that one end is shallower to allow for the JST connector, and at the other end the internal rim of the cover allows for a snug fit at the USB-C end.

38. Fit the battery (6) with one or more rubber bands of thickness sufficient to ensure that it will not inadvertently slip from the battery slot on the side of 3D printed XyloPhone housing (1). Slide the battery into the slot. Plug the male JST connect from the battery into the power input JST on the electronics compartment for use, or remove the charger cap and plug it into the charger if the battery needs to be charged. The charger cord (8) plugs in at the USB-C end, and can be charged with any typical 5V cell phone charging block or USD port on a computer.
39. Ensuring that the lens from the Belomo 10X triplet loupe (9) is free from fingerprint and dust on both faces, place it into the central cylindrical opening in the 3D printed XyloPhone housing (1). Press it into place until it reaches the 3D printed stops.

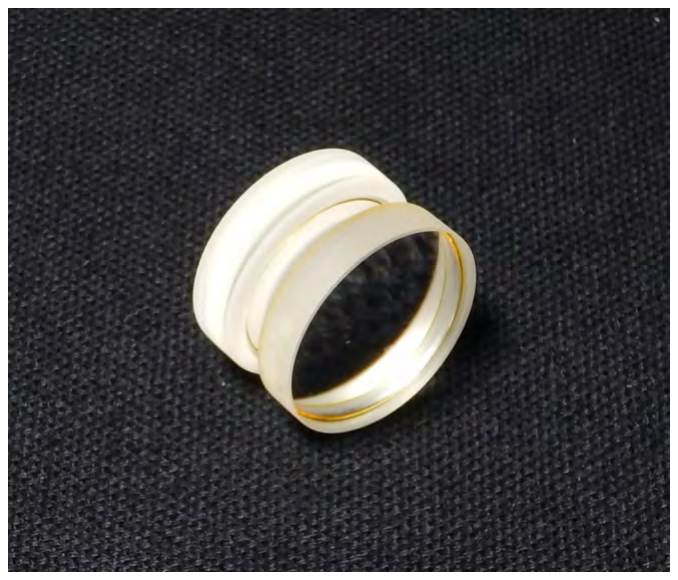
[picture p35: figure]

40. Place the 3D printed spacer ring (4) into the central cylindrical opening in the 3D printed XyloPhone housing (1). Press it into place firmly.

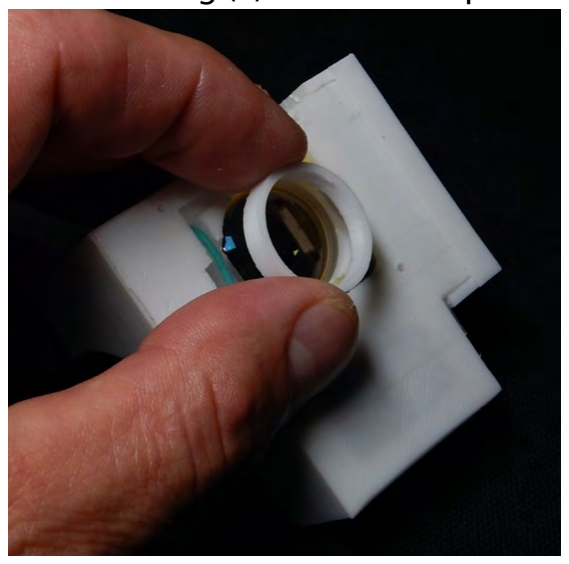
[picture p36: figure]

41. This completes the XyloPhone imaging and lighting unit. What remains is to attach the XyloPhone to a customized base or mount for your phone. We have provided the basic 3D file for the XyloPhone-to-smartphone interface; the center point of the four mounting screws holes is the center of the light path in the XyloPhone. It is incumbent on the user to develop a phone-specific interface. Below we show two such interfaces. One slides over the phone with no case, is held in place by friction, and is good for lab work or extended use of the XyloPhone for data collection. The other is a “paddle” design that fits into the smarthphone case, but must be held in place by the user. This is convenient for intermittent and field use where it is helpful to keep the phone protected in its case.

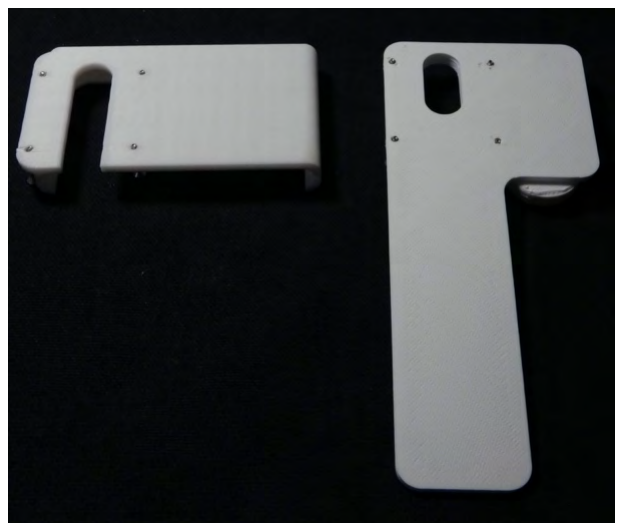
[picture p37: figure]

42. Mounting the XyloPhone to either base is the same process; using four ½” No. 2 screws (16a), screw the XyloPhone onto the base, being careful not to overtighten the screw and strip the plastic in the XyloPhone. Depending on the orientation of the XyloPhone and the design of the phone base, it can be necessary to adjust the design of the 3D printed charger cap (2) so that the lower edge of the cap does not interfere with the base.

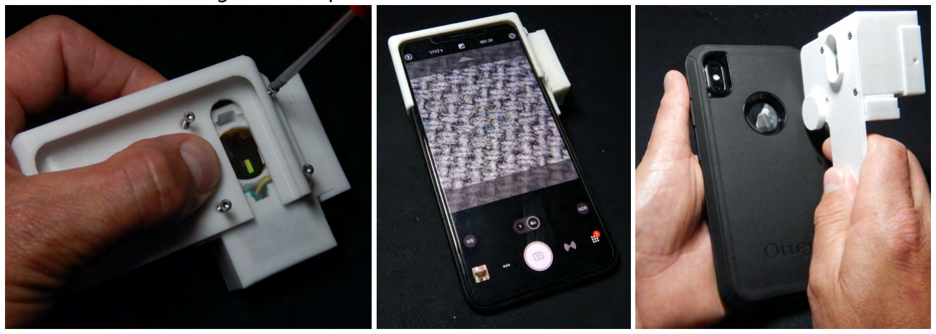
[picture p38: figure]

Note that depending on the lens-switching parameters of your specific phone, the default camera app native to your operating system may not suffice to operate the XyloPhone; you may need to purchase or otherwise acquire a third-party camera application that allows you to control the camera(s) as needed.

You have constructed a new XyloPhone – your skills are complete.

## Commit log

2020-10-16 Commit of gerbers and 3d files for xylophone
    [UV mounting jig.stl, XyloPhone_housing.stl, charger_cap.stl, electronics_lid.stl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]
2020-11-21 Bill of materials added
    [XyloPhone bill of materials.xlsx]
